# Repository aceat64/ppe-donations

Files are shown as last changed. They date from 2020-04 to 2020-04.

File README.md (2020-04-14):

DFW PPE

# Donation Instructions
The Coronavirus Pandemic (COVID-19) has placed a great strain on the supply chains for various kinds of Personal Protective Equipment (PPE) desperately needed by those working the front lines in the fight against the disease. Due to the widespread availability and private ownership of 3d printers and sewing machines, we have a way to fill some of the gaps in PPE availability. But just building PPE isn’t enough, we need to do our best to ensure what we build is safe, reliable and easy to use. The primary goal of our work is to build face shields, based off a design approved for use by the U.S. Department of Health and Human Services - National Institutes of Health (NIH). The procedures we’ve built allow us to do our best to establish a “chain of custody” that will help ensure the PPE we provide has not been compromised.  

**Please read these instructions carefully, and follow them as well as you are able. It is vitally important.**

Before starting, please read and agree to the following:

1. I will not participate if myself or anyone in the household is sick or shows signs of Coronavirus.
2. I will do my best to ensure the materials I produce are safe and clean.
3. I will follow the guidelines for as best as I can.
4. I will do my part in limiting the spread of Coronavirus by going out only when required and by maintaining social distancing.

## Updates
Please check back at this page frequently, as we may make changes to process, best practices and donation drop-off locations.

## What We Need
There are 3 primary categories of items we need. Headbands printed on 3d printers, sewn ties to hold the headband on the user’s head and certain types of plastic sheets that can be used as improvised visors for the NIH approved face shield design. While many people have used this design with elastic straps or rubber bands, the input we’ve received from end-users is that ties are superior, as it allows them to pick the tightness they prefer, which increases comfort and allows them to wear the face shields for longer.

### 3D Printed Headbands
1. Download and print the headband STL file, link below. You may use ABS, PLA, PETG, ASA and Nylon.
  * [NIH - DtM-v3.0 Face Shield PPE, 3D printable headband
](https://3dprint.nih.gov/discover/3dpx-013359)
  * [Archive.Org Backup](https://web.archive.org/save/https://3dprint.nih.gov/discover/3dpx-013359)
  * The STL file itself is also available in this repo, but please use the NIH website as there may be critical updates to the design.
2. Thankfully the temperatures involved in 3d printing are high enough to mostly ensure the print will leave the printer clean. It is up to you to ensure it stays that way.
3. When the print completes, do not touch it until you have cleaned your hands. If possible wear new/unused gloves as well. Follow [CDC guidelines on handwashing](https://www.cdc.gov/handwashing/when-how-handwashing.html).
4. Most prints will come with rough or sharp edges on the parts of the headband that touch the user’s forehead. These edges can be cleaned up before the part is donated, but if you can't do so while keeping the part sanitized don't worry about it, we can clean up the edges during assembly.
  * Ensure that any tools you use to clean the part have been sanitized with alcohol wipes or other cleaning solutions that are confirmed effective against Coronavirus.
5. Once the part is clean and ready to be donated, place it in a clean and sealed plastic bag (e.g. a ziplock bag).
6. Write your name and the date the part was sealed on the outside of the bag.
7. Do not open the bag again.
8. Follow the Donation Drop-Off Instructions at the end of this document, to donate the headband at one of our donation drop-off points.

### Fabric Ties
Fabric ties allow the wearer to tighten the face shield to fit their head, which helps keep it comfortable. Specifically we are looking for ties that are about ⅜” wide and about 24” long. There are many ways to accomplish this and whatever works best for you is acceptable, as long as the cleaning procedures are followed.

#### No Sewing Method: Making Ties Out Of T-Shirts
This is the fastest and easiest way to make useful ties! We've also found these ties are much easier for us to use when assembling face shields. Instructions with pictures are in the [tshirt ties](tshirt_ties.md) file.

#### Bias Tape Method: Making A Sewn Tie With Basic Sewing Tools
1. Finger press 1 ½” strip of fabric in half.
2. Fold each side in to meet in the middle.
3. Fold in half again, so that the two folds meet, it should be about ⅜” wide at this point.
4. Stitch down the edge as closely as possible.
5. Cut to 20"-24" (it doesn't need to be precise), optionally sew ends to keep them from unraveling.

Check out this great YouTube video for a simple trick to make this easier: https://www.youtube.com/watch?v=vR7sWFwo48g

#### Cleaning Fabric Ties
1. Wash the completed ties using soap and a small amount of bleach.
2. From this point forward, do not touch the ties except with freshly washed hands. If possible wear new/unused gloves as well. Follow [CDC guidelines on handwashing](https://www.cdc.gov/handwashing/when-how-handwashing.html).
3. Using freshly washed hands, move the washed ties to your dryer.
  * Some people have had better luck air drying the ties, as they can get rather tangled in the dryer.
4. Once dried, again use freshly washed hands (additionally you can use clean/unused gloves) and place the ties in a clean and sealed plastic bag (e.g. a ziplock bag).
5. Write your name, the number of ties and the date on the outside of the bag.
6. Do not open the bag again.
7. Follow the Donation Drop-Off Instructions at the end of this document, to donate the headband at one of our donation drop-off points.

### Commercially Available Improvised Plastic Visors
The clear “visors” we are improvising for this design can come from a number of sources. The best are clear binder dividers with pre-punched holes. We prefer that the visors be delivered still in their commercial packaging, unopened. This helps ensure they are clean.
Example Visor Options
* Avery Clear Easy View Durable Plastic Dividers Item 16741
* Office Depot "clear gloss poly binding cover" Item 459-207 
* Fellowes 52311 Crystals Presentation Covers with Round Corners, 8mil 11 1/4 x 8 3/4, Clear (Pack of 100)

#### Donating Improvised Plastic Visors
1. Do not open the commercial packaging.
2. Do your best to handle the packaging so that it remains clean. Wash hands before touching it, wipe it down with a cleaning solution, etc.
3. Write your name and the date of donation on the packaging.
4. Follow the Donation Drop-Off Instructions at the end of this document, to donate the visors at one of our donation drop-off points.

## Donation Drop-Off Instructions
**Please be sure you followed the instructions above for the items you have produced/procured. Donations that do not match our criteria or do not follow the rules will be discarded for safety.**

1. Before leaving home, check your temperature with a thermometer. If you have a fever or any other symptoms, DO NOT PARTICIPATE.
2. IF ANYONE IN YOUR HOUSEHOLD IS SICK, DO NOT PARTICIPATE.
3. If someone else is dropping off materials when you arrive, wait in your vehicle until they are done. Maintaining social distancing helps prevent the spread of Coronavirus.
4. If possible, please use hand sanitizer to clean your hands, and put on clean/unused gloves before exiting your vehicle.
5. Place your items in the donation box as indicated by signage.
6. **IMPORTANT!** Record your donation using [this form](https://docs.google.com/forms/d/e/1FAIpQLSeufs_A6_XCnf65XNlsDAwN6ECZPi3XLqRlp83tyoBMacYtQw/viewform).
7. Don’t forget to wash your hands when you get home. Avoid touching your face.

### Drop-Off Locations
#### Dallas Makerspace
[1825 Monetary Lane, Suite 104, Carrollton, TX 75010](https://goo.gl/maps/YAHaSz75sjb2BRur7)

Drop-off is open 24/7. Donation boxes are black and yellow, located out front.

Dallas Makerspace donation drop-off boxes

## Where Are These Going
The first few rounds will be going to Scottish Rite hospitals. If you represent a DFW area medical facility, first responder group (FD/PD/etc) or another group on the front lines that needs face shields, please reach out and let us know what you need.

## Use Our System
Do you want to use these instructions and files to setup a similar system? GOOD! Do it! **You don't need to ask, everything here is free to use without restriction.** Just promise that you'll do your best to help out, even if that means realizing the best way to help is by simply staying home and keeping the virus from spreading.

## Other Donations
We are not accepting any other kinds donations. If you have commercial PPE or anything that could be useful, please donate it directly to an organization that can use it.

There are number of awesome groups out there coordinating manufacture and distribution of sewn face masks. If you're building these kinds of masks please check them out! One example is the Facebook group [SewStrongDallas](https://www.facebook.com/groups/3685675388169253/).

## Contact Us
If you'd like to contact us about this initiative, please send an email to ppe@beyondweb.net

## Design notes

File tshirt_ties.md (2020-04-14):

# Making Ties Out Of T-Shirts
1. Lay an Adult size t-shirt on cutting mat. Cut off and discard the hem.
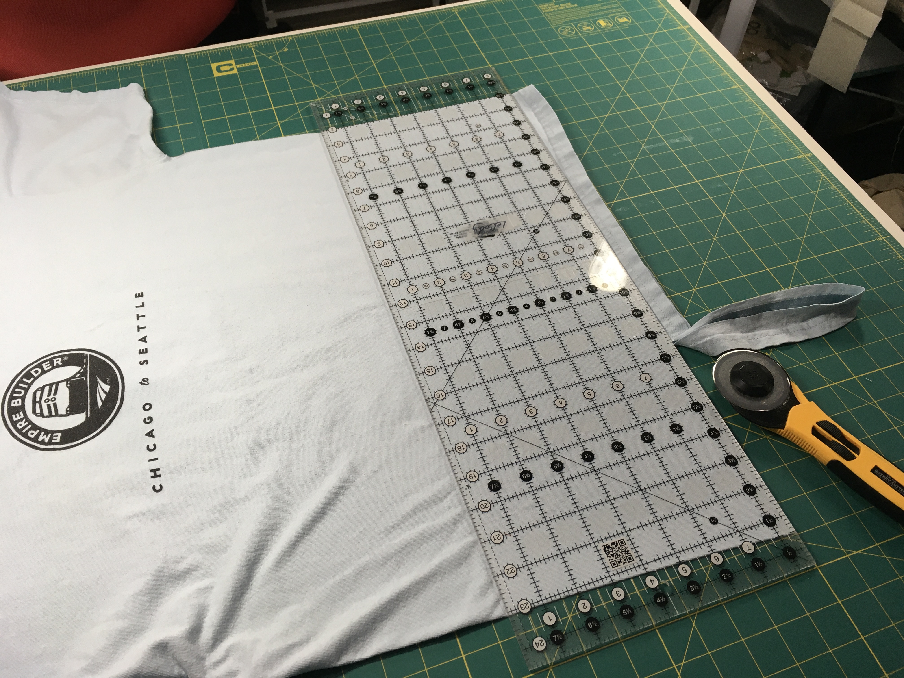
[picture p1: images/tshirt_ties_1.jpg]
step 1


2. Using the widest ruler available and a rotary cutter, set the ruler’s 8 inch marking on the cut edge(the clean cut that removed the garment’s hem).
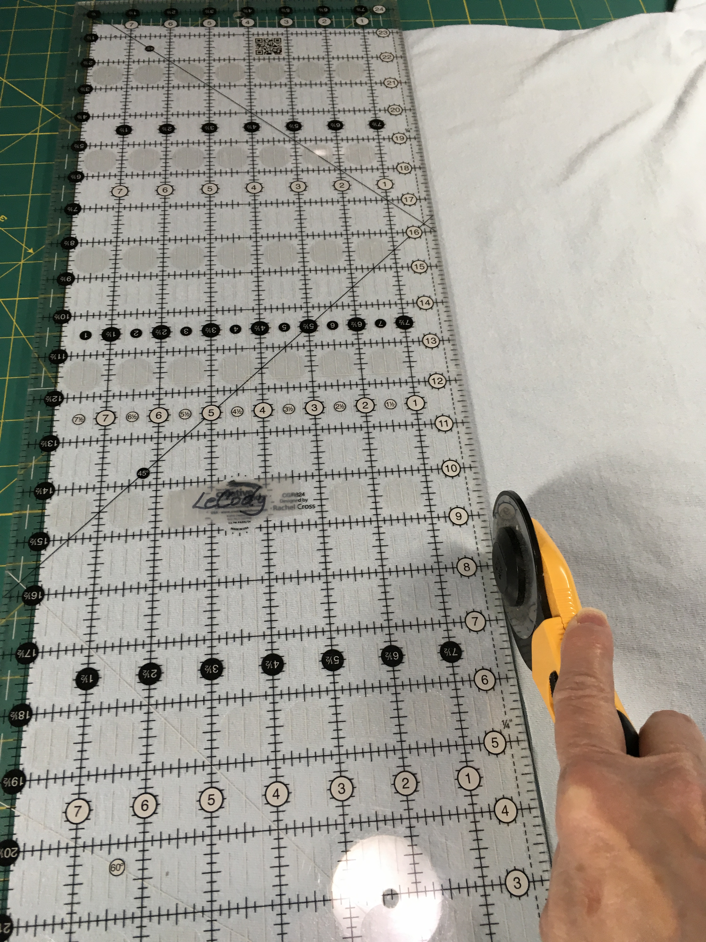
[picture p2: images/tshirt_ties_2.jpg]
step 2


3. Cut the 8” wide strip down to eight 1” wide strips simply by moving the ruler to the left an inch at a time.
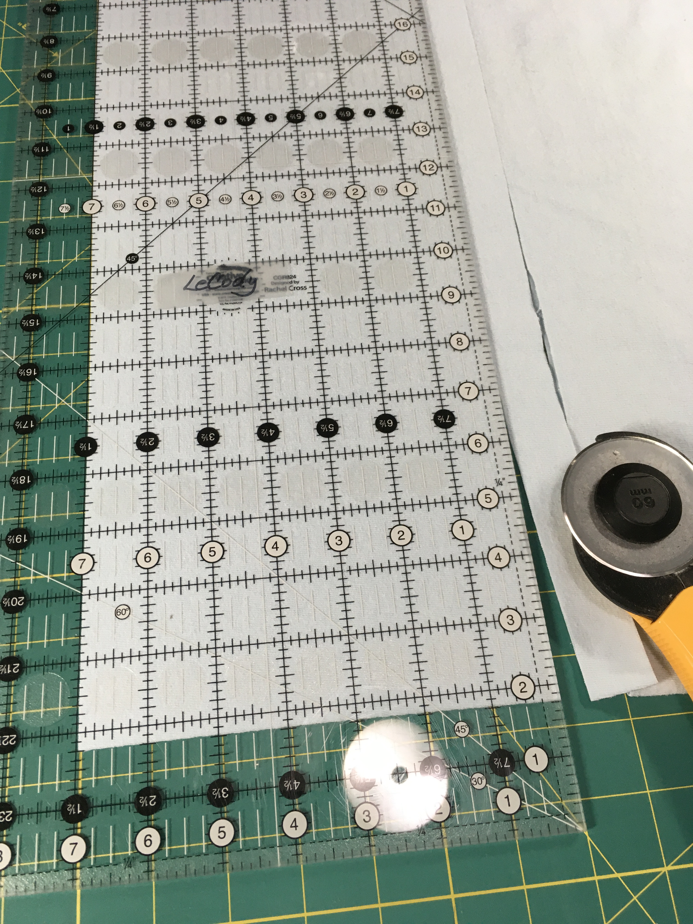
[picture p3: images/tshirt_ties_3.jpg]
step 3

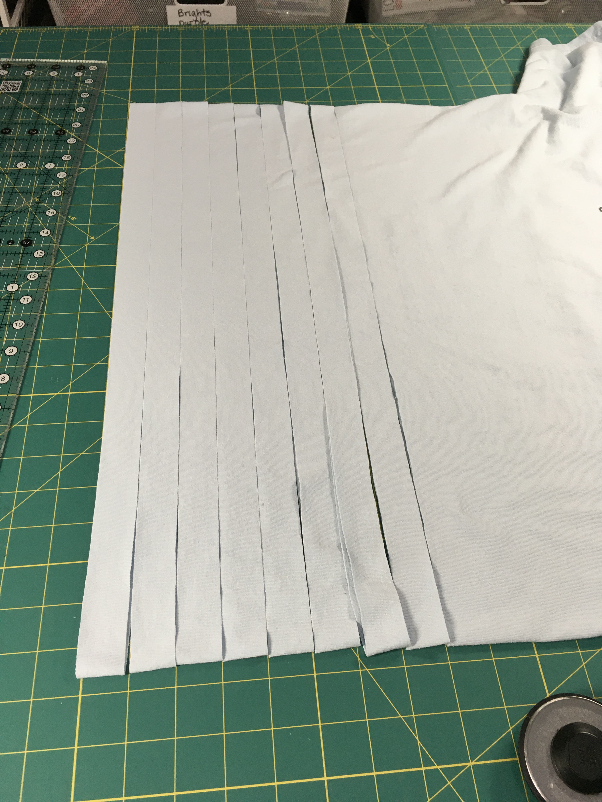
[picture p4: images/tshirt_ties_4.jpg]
step 3a


4. Pick up each loop and stretch it as far as it will stretch.  Doing this causes the loop to roll up on itself. It can then be cut to whatever length is needed.
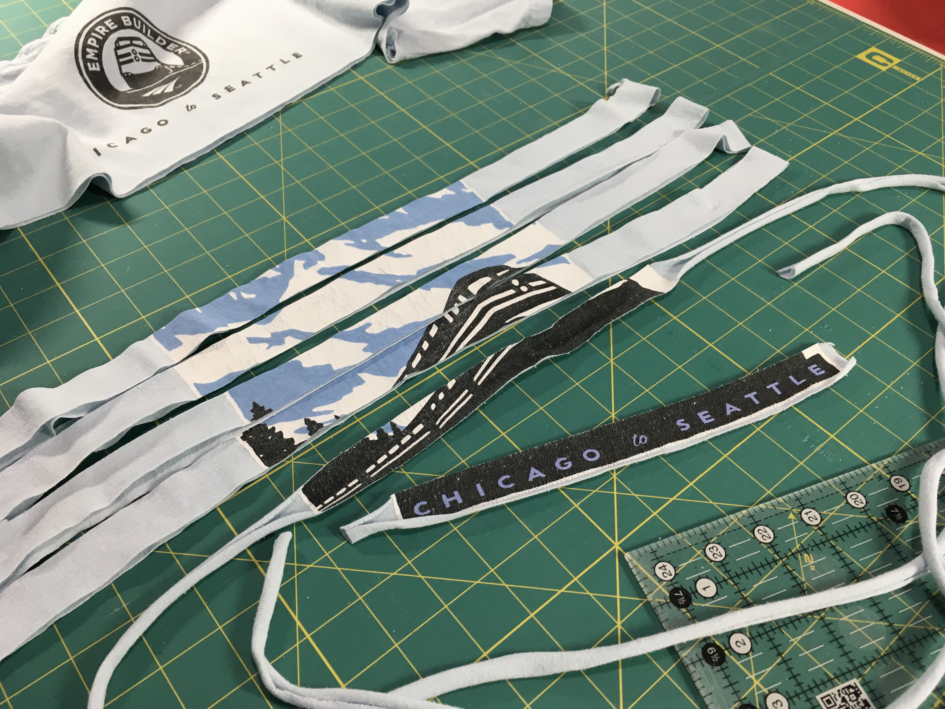
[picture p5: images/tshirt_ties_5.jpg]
step 4


Notice that t-shirts with a big printed image won’t roll up. You can simply discard those parts of the loop that won’t roll.

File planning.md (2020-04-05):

# General Overview
This document covers some of the assumptions and design criteria we used when developing the system.

1. Sourcing of materials is primarily left to the crowd.
1. Instructions given to the donors/volunteers will always emphasize the importance of keeping items cleaned and sterile.
1. We will assume that all items are given to us contaminated and need to be cleaned in some way.
1. We will use Google Forms and Sheets to help establish a chain-of-custody from donor to point of delivery.
1. People print headbands at home, sew ties at home, and acquire needed supplies when going out for groceries. Donors MUST NOT make trips out specifically for this, limit interactions with others (ideally avoid physical interactions entirely), everyone must do their part to prevent the spread of this virus as much as possible.
1. We expect all donors to follow our guidelines for keeping items as sanitized as possible before drop-off.
1. Donors write their name and date on donation, so we can start tracking for chain-of-custody.
1. At drop-off, donors submit a Google Form detailing what they dropped off and when.
1. Volunteers verify and record the donation in batches, using a Google Sheet.
1. Batches are sanitized at one or more specifically setup and cleaned places, following detailed procedures for how to sanitize and track.
1. Once boxed, donations are placed in a specifically designated and cleaned area before being transported to destination.
1. Material donations that do not match criteria are DISCARDED, material donations that are not labeled with donor name and date or are not submitted with Google Form are DISCARDED. No exceptions. All deviations from the process are DISCARDED. This helps ensure that the face shields we provide are clean, safe and as close to medical-ready as possible.
1. Hospitals will ideally wash the shields and materials after receiving them, for additional protection.
1. We have some capacity for UVC sanitization, this will be used for shields that will be sent to hospitals.
1. When we have more materials than our ability to UVC sanitize, we will clean and sanitize them as best as we can.
1. All packages will be sealed and labeled with information such as batch number, sanitization that was performed, quantity of headbands and visors, etc.

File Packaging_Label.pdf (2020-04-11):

# Face Shields

Quantity | __________ Headbands with: ties elastic __________ clear visors
Model ID | 3DPX-013359
URL | https://3dprint.nih.gov/discover/3dpx-013359
Design Approval | NIH Approved Design
Components | Headband - 3D printed (various materials, may be ABS, PLA, or others) Ties - Fabric, sewn Visor - Commercial available plastic sheets/transparencies

# Batch Information

Batch Number

Assembly Date

Assembly Location

Cleaned? | Y / N
UVC Sanitized? | Y / N

Other Notes

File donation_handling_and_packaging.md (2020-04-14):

# Donation Handling And Packaging

## Rules For Volunteers
1. Before leaving home, check your temperature with a thermometer. If you have a fever or any other symptoms, DO NOT PARTICIPATE.
1. IF ANYONE IN YOUR HOUSEHOLD IS SICK, DO NOT PARTICIPATE.
1. If anyone in your household becomes sick, notify coordinators IMMEDIATELY.
1. Maintain 10 feet distance from each other at all times.
1. Wear masks and fresh gloves at all times when in the same room as the donations/PPE.
1. Wash hands with soap for at least 20 seconds upon arriving. Follow [CDC guidelines on handwashing](https://www.cdc.gov/handwashing/when-how-handwashing.html).
1. Regularly re-wash hands. Again, follow [CDC guidelines on handwashing](https://www.cdc.gov/handwashing/when-how-handwashing.html) (can not be stressed enough).

## Collection and Processing Procedure
### Processing Site Setup
* The site is thoroughly cleaned before each batch.
* After the site is cleaned, all gloves that were worn are discarded and everyone washes their hands again.
* The processing site consists of a "clean" and "dirty" area.
* The dirty area is where materials are placed prior to and during intake.
* The clean area is for all steps after the intake wash and rise.
* Anyone who has been in the dirty area MUST NOT enter the clean area until they have discarded their gloves, washed their hands and put on a clean pair of gloves.

### Processing Steps
1. A new batch number is created.
1. Donations from the drop-off box are verified against donation receipts from Google Form.
1. Unknown donations or donations that do not follow our criteria are DISCARDED.
1. Separate plastic, ties and prints into groups on a table with a batch number sign/placard. Be sure not to mix with other batches.
1. Record verified donations in Google Sheet for the batch number.
1. Materials are then moved to sanitization, and recorded in Google Sheet.
1. Sanitization is done in the following wet process steps:
  1. Intake wash with soap and water.
  2. Intake rinse with clean water.
  3. 20 minute soak in Steramine (or similar) solution.
  4. Rise with clean water.
  5. Air dry.
1. Additional sterilization is done with UVC light. Parts sterilized with UVC are not mixed with non-UVC sterilized parts, packages will indicate if the parts went through the UVC process.
1. Once all items are clean, the ties are tied onto the headbands.
1. 24 headbands (with ties) and at least 24 clear plastic visors are placed into a box and sealed.
1. Sealed packages are marked with the date, batch number, type of cleaning/sterilization performed and a description of contents.
1. Sealed packages are placed in the designated storage area to await transport.
1. Total number of packages and their contents are recorded in Google Sheet.
